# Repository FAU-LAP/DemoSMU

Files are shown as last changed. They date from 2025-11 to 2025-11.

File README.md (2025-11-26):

# DemoSMU

This repo contains all necessary information to build and use the DemoSMU, a tiny source-measure unit (source and measure voltage &amp; current) built from an Arduino Nano 33 IoT.

https://github.com/user-attachments/assets/6f9243c5-a85d-4b45-aedf-7c95de8d8e7f

Here we use the DemoSMU to perform a simple current-voltage measurement of a diode using NOMAD CAMELS to control the instrument.

## Arduino Nano 33 IoT

The Arduino Nano 33 IoT is a small, powerful board based on the SAMD21 microcontroller. The board operates at 3.3V and has a variety of analog and digital pins for interfacing with sensors and other components. It costs around 20€ to 30€.

Its `A0` pin is used as a DAC (Digital-to-Analog Converter) to output voltage or current, while the `A7` pin is used as an ADC (Analog-to-Digital Converter) to measure voltage or current. To measure the current, the voltage drop between `A1` and `A7` is measured and divided by the known shunt resistor value (100 Ohm recommended).

## Setting up the Arduino Nano

Load the provided Arduino sketch `/Arduino_code/k2400_emulator.ino` onto the Arduino Nano 33 IoT using the Arduino IDE.

You can modify the shunt resistor value in the sketch if you are using a different value than the recommended 100 Ohm. This is done on line 24:

```cpp
static const float SHUNT_RESISTANCE = 96.6f;    // ohms (adjust to your shunt)
```

The `.ino` assumes you are using a reference voltage of 3.3V. Adjust line 23 if this is not the case.

> [!NOTE]
> The Arduino Nano is emulating a Keithley 2400 SourceMeter, so you can use any software that supports the Keithley 2400 to control the DemoSMU. This is tested using [CAMELS](https://fau-lap.github.io/NOMAD-CAMELS) and provides a very simple source-measure unit that can be integrated into existing setups easily.

Reading voltage and current samples 100 times. The average of these samples is used as the measurement result. This helps to reduce noise in the measurements. To change this, modify lines 82 and 90.

When setting the voltage it iterates 10 times to get the best match of read value to set point, for setting current it does this 75 times. To speed things up you can reduce this by changing lines 191 and 276.

## Hardware Setup

Requirements:

- Soldering iron
- 2x short wires
- 100 Ohm resistor
- 3D printed case and lid (optional, `.stl` files in `/3D_printing`)

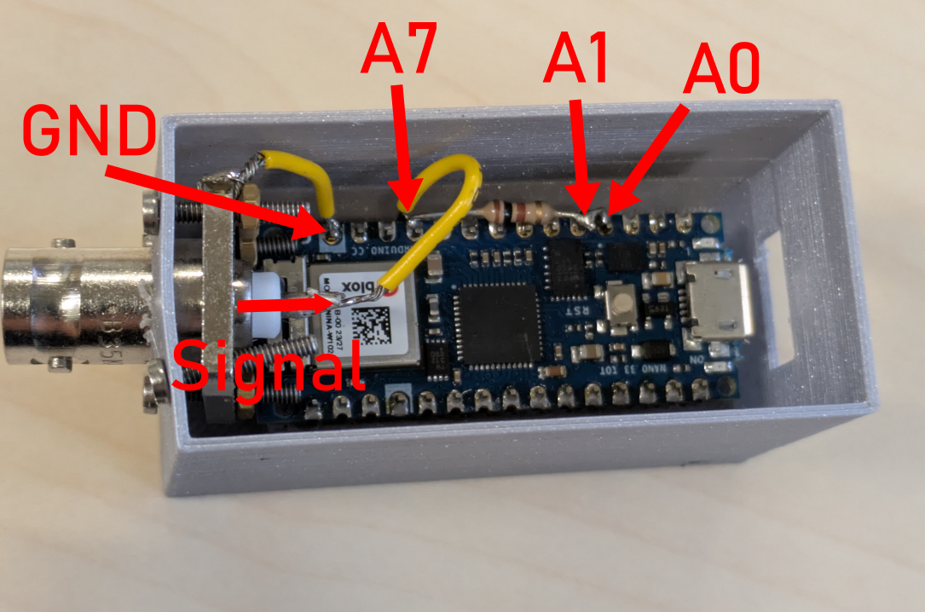
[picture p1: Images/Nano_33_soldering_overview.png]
Layout for soldering

Steps:

1. Solder 100 Ohm resistor to pin `A0` and `A7`.
2. Connect `A0`and `A1` directly.
3. The device under test (DUT) should be connected between `A7` (positive terminal) and `GND` (ground). In the image above we use a simple BNC connector for this, but any other connection (like a simple wire) to your DUT works as well.

### 3D printing

The `.stl` files for a simple case and lid are provided in the `/3D_printing` folder. The case has a hole for a BNC connector, but you can also simply connect wires to the `A7` and `GND` pins if you do not need a connector.

## Connect the Arduino to your PC

Use a USB cable to connect the Arduino with your PC. The Arduino will create a virtual COM port that can be used to communicate with it.

## Using the DemoSMU

For measurement software the connected Arduino is a Keithley 2400 SourceMeter. You can use any software that supports this device. 

### Available Commands

> [!NOTE]
> Only voltage and current can be read and set. Does not support reading resistances directly.

The following SCPI commands are supported:

|Command|	Type|	Description|
| --------|--------|--------------|
|*IDN?	|Query	|Returns the identification string: Arduino,Nano33IoT,SCPI-Emulator Keithley 2400,1.0|
|:CONF?|	Query|	Returns the currently configured measurement function ("VOLT", "CURR", or "RES").|
|:READ?|	Query|	Performs the measurement based on the current configuration (voltage or current) and returns the result as a single float.|
|:SOUR:VOLT <value>|	Command|	Sets the output voltage to the specified value in volts.|
|:SOUR:CURR <value>|	Command|	Sets the output current to the specified value in amperes.|
|:OUTP ON|	Command|	Enables the output. Currently does not do anything!|
|:OUTP OFF|	Command|	Disables the output. Currently does not do anything! |

The Arduino will ignore most commands it does not support silently. To add functionality or change it, modify the `.ino` file.

## Accuracy and Limits

The voltage and current setting is not very accurate due to the limited resolution of the DAC and ADC on the Arduino Nano 33 IoT. The voltage can be set with a resolution of approximately 3mV (3.3V with 1024 steps). The maximum output current of the Arduino is 7mA.

## Dimensions

The dimensions of the DemoSMU (the case) are approximately 60mm x 30mm x 40mm.
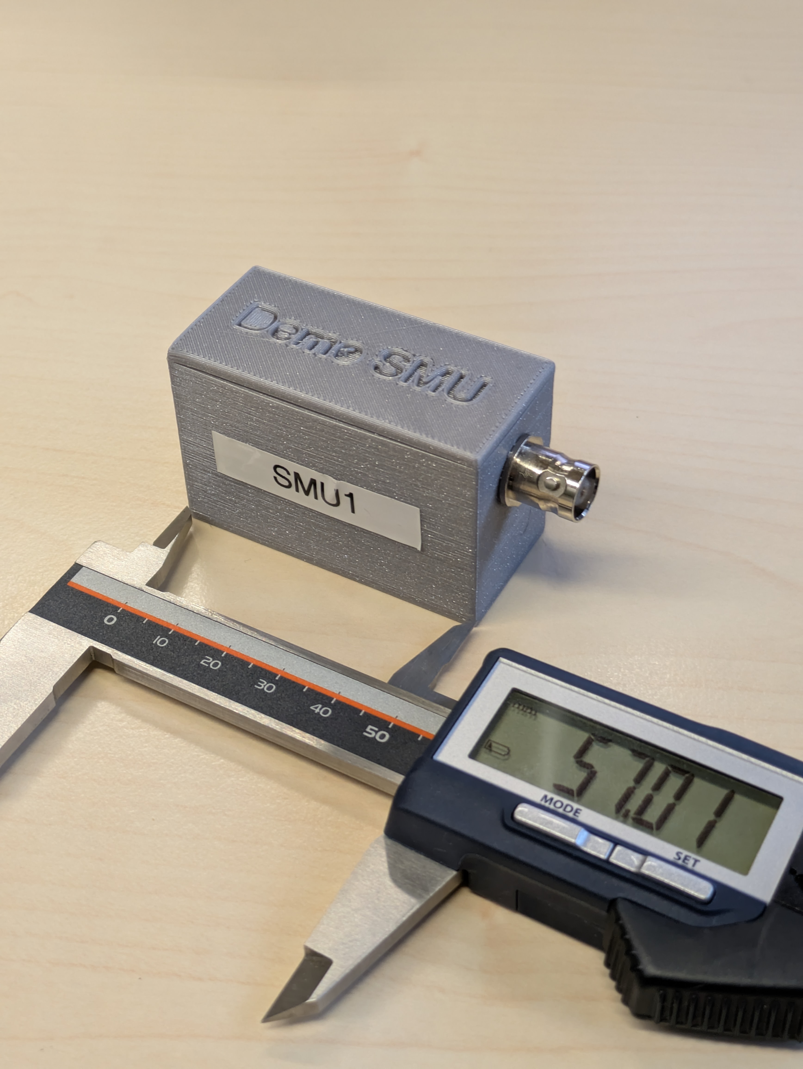
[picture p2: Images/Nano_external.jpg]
Size overview


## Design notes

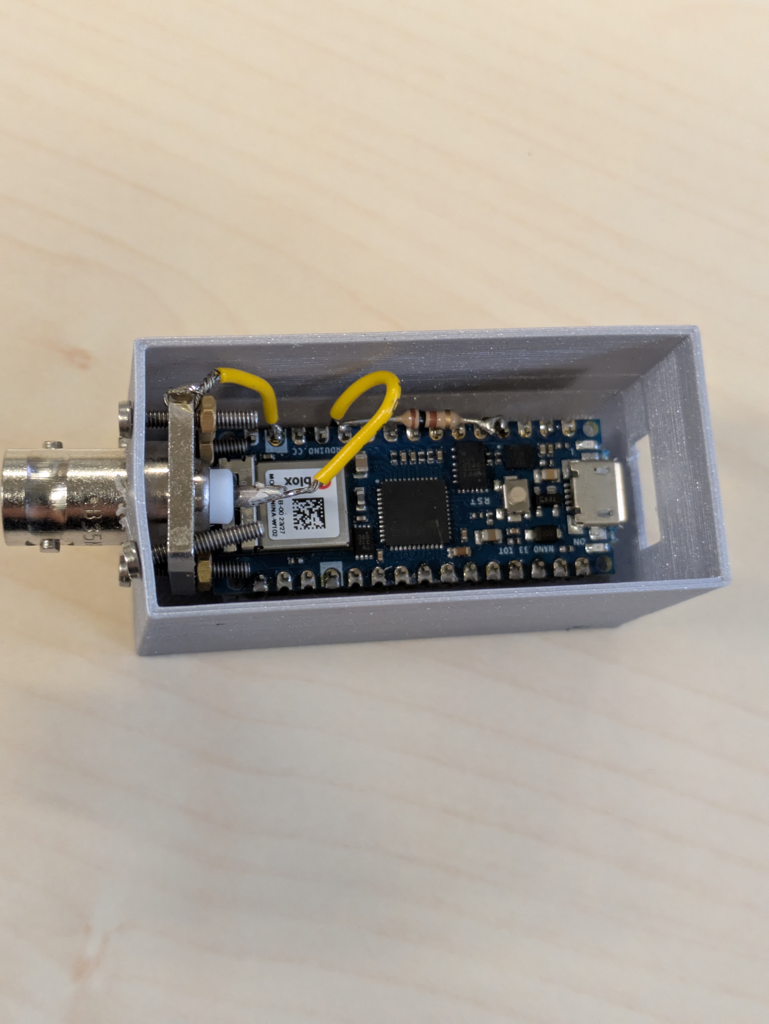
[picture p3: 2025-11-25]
Images/Nano_internal.jpg

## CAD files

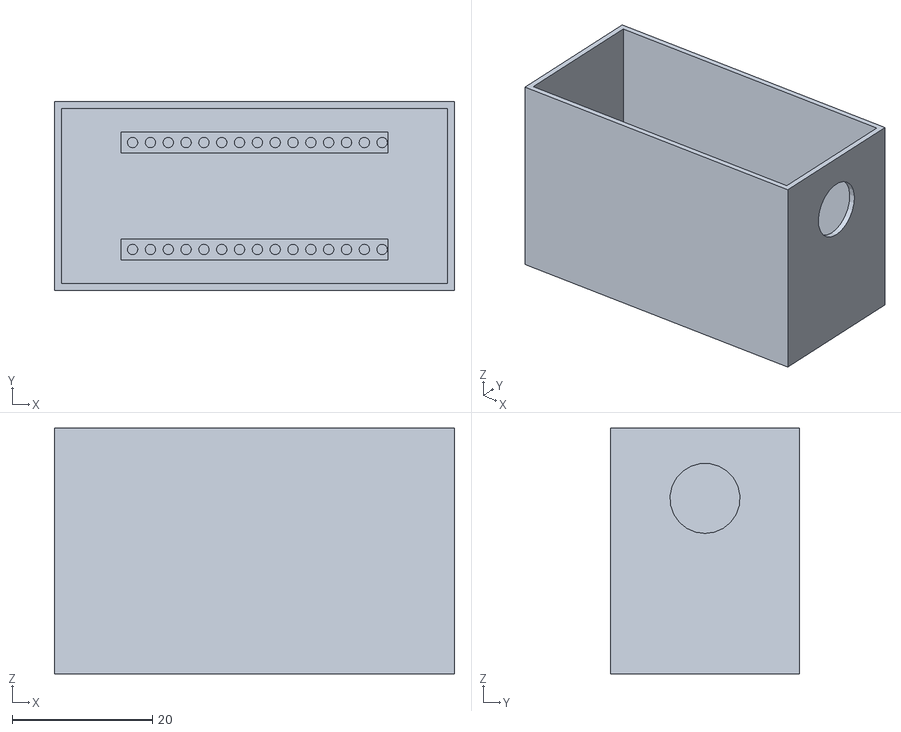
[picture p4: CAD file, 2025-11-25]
3D_printing/Arduino_Nano_33_Case_SMU.stl
57.0 x 27.0 x 35.0

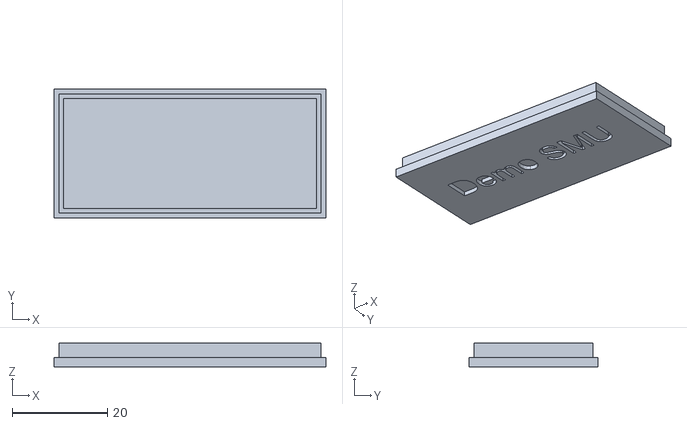
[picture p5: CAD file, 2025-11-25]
3D_printing/Arduino_Nano_33_Lid_SMU.stl
57.0 x 27.0 x 5.00
